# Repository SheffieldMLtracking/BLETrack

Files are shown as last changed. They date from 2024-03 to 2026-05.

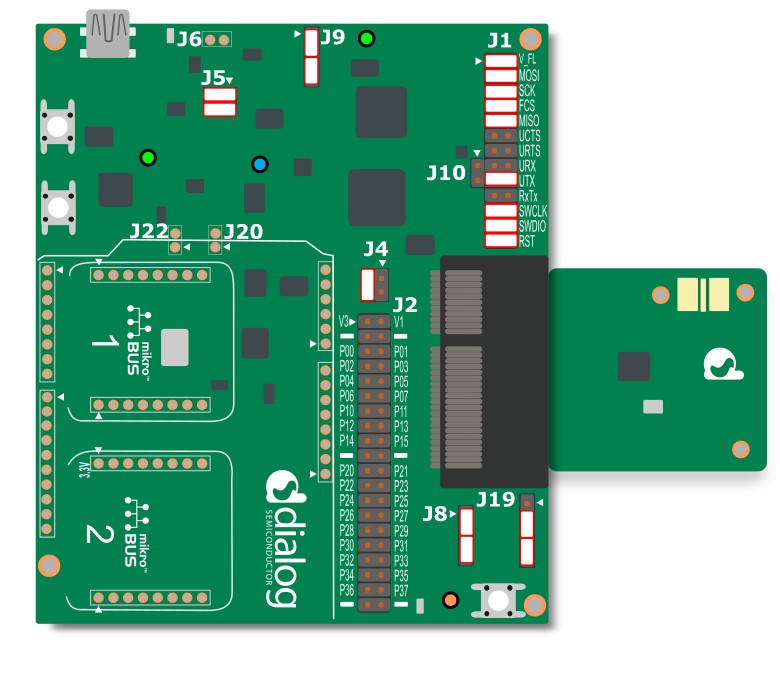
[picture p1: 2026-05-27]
Receiver/nestfinding adc recording/active_scanner/assets/da14585.jpg

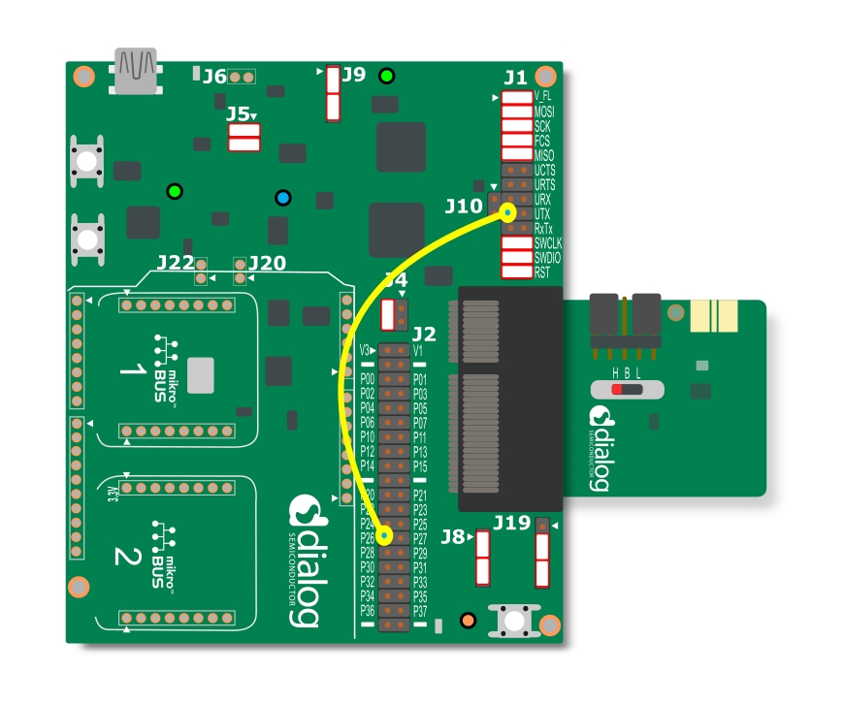
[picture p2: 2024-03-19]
Receiver/nestfinding adc recording/active_scanner/assets/da14531.jpg

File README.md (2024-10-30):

path

Code for Bluetooth Low Energy bee tracking system.

+ "Transmitter" folder contains the code to be flashed to the BT832X/BM832E transmitter board.
+ "Receiver" folder contains the code to be flashed to the DA14531 chip on-tag and the 'Active Scanner' code for testing & diagnostics.
+ "To Print" folder contains [FreeCAD](https://www.freecad.org/) files of the transmitter housing.
+ "Path Inference" folder contains code to process data from tag/dev board
+ Test data stored [here](https://github.com/SheffieldMLtracking/bluetooth_experiments)

## Notes on Programming Transmitter
### Transmitter programming:
+ Requires [nRF Connect SDK](https://www.nordicsemi.com/Products/Development-software/nRF-Connect-SDK).
+ Create a build for the nrf52dk_nrf52832 and add the included device tree overlay.
+ Connect nrf52dk and BT832X/BM832E to the computer via JLINK (done via micro USB cable). Connect DEBUG OUT on nrf52dk to DEBUG IN on BT832X/BM832E:nrf52dk_programming_example
+ flashthisfirst.c must be flashed to the BT832X/BM832E first - then main.c can be flashed.

NOTE: P0.31 is used for encoder output A, P0.30 for encoder output B and P0.11 for hall effect sensor input.

### Receiver programming:
+ Requires Keil uVision and configuration of environment as shown [here](https://lpccs-docs.renesas.com/UM-B-117-DA14531-Getting-Started-With-The-Pro-Development-Kit/01_abstract/abstract.html).
+ To program a receiver tag via flashing code to the OTP memory, follow [these](https://lpccs-docs.renesas.com/Tutorial_SDK6/otp_prog.html) instructions. **If you need to debug code on a tag, do not flash to the OTP.** DA14531 USB Development Kit can be used as a serial wire debug probe to debug code on an external DA14531 chip on the receiver tag using [this](https://lpccs-docs.renesas.com/Tutorial_SDK6/debug_probe.html) configuration of SWIO cables and DIP switches.
+ Note: binary for compiled DA14531 is found in Keil/DA14531_OUT/Objects.
+ Note: USB dev kit switches should be configured as shown: da14531_usb

## Usage of the System
### Setting Up Transmitters
+ Charge transmitters before field trial!
+ Each transmitter is placed onto a tripod across the landscape. The 0 degree point on the tripod (denoted by the small magnet on the base the transmitter sits in) should be pointed north using a compass before placing the transmitter itself upon the tripod. The transmitter should be level with the ground and mounted as high up as possible.
+ As each transmitter is turned on, the time between turning each on should be taken using a stop watch. This time is later used to zero the time readouts in the packets.
+ Using the "Active Scanner" code downloaded to the DA14531 USB Dev Kit, the serial output from the dev kit - which can be accessed using a serial terminal program such as Tera Term - should be used to verify the functionality of the tramsitters. The packets recieved by the active scanner are in the following form and should be assessed to ensure that the transmitter is in fact transmitting and that the motor is reading out ~360 degrees of rotation, resetting at the zero point. If there is an issue, the transmitter may need reprogramming, regarching or the motor encoder may have been knocked out of place.
Screenshot from 2024-10-29 13-43-06
+ Each transmitter currently has a range of approximately 100m (further at peak signal strength but not currently used in angle inference algorithm). The area tracked should be covered by at least 2, preferably 3 transmitters.

### Using a Receiever Tag
+ A programmed tag should be allowed to drain fully to hardware reset, then be charged and attatched to a bee.
+ Following retrieval, put the tag on charge and apply ground to the interrupt pin to switch the tag into transmit mode.
+ The data of each packet is encoded in the destination addr, in the same form as the transmitted packets except the RSSI of the packet is encoded in the leftmost byte. Using a bluetooth sniffer (reccomended [nrf52 BLE sniffer](https://www.nordicsemi.com/Products/Development-tools/nRF-Sniffer-for-Bluetooth-LE)) and Wireshark the transmitted packets can be read. The following filter shows only read packets:
<p align=center>btle.advertising_header.pdu_type == 0x01 && !_ws.expert && btle.advertising_address == 80:ea:ca:70:00:04</p>

### Performing Infernece
+ Instructions for performing path inference on data are located in PathInferenceFinalCut.inpyb

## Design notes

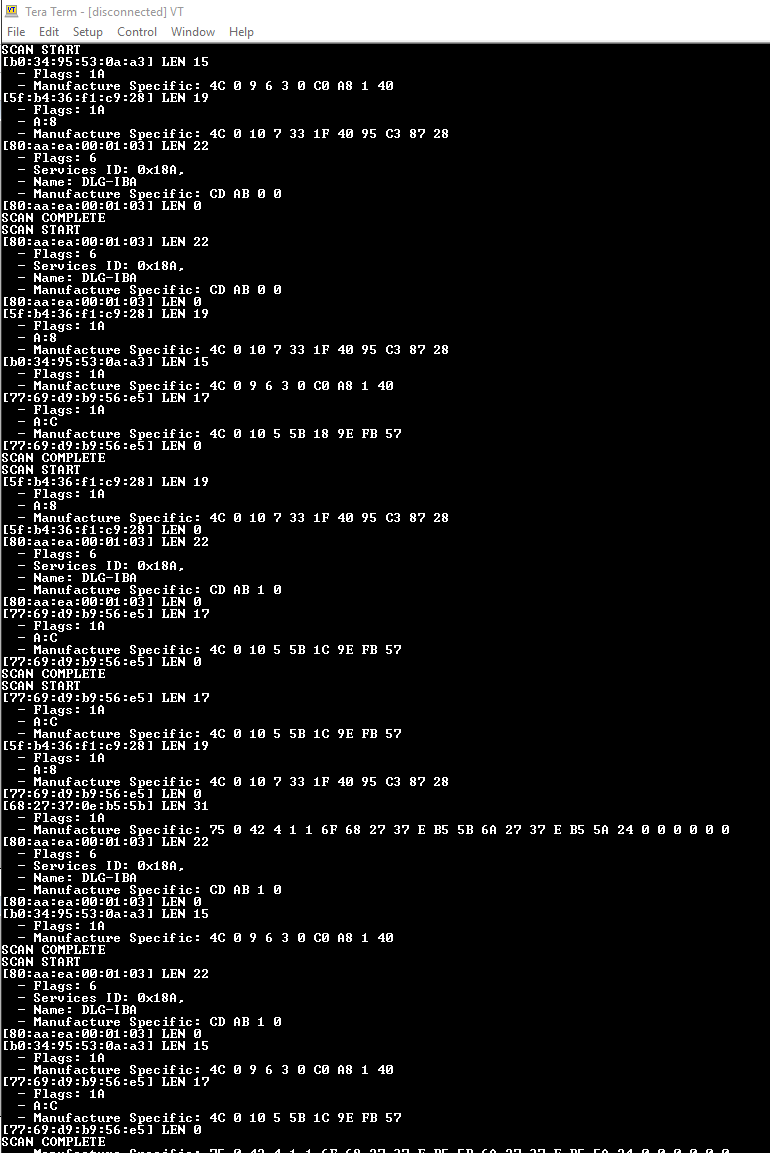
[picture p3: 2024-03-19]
Receiver/accel/active_scanner/assets/active_scanner.png

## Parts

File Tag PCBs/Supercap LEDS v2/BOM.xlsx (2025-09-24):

 |  |  | xxxx xxxx xxxxx xxPCS BOM (Sample Bill of Materials)
Item # | *Designator | *Qty | Manufacturer | *Mfg Part # | Description / Value | *Package/Footprint | Type | Your Instructions / Notes
1 | C1 | 2 | KYOCERA AVX | CM05X5R226M04AH | Multilayer Ceramic Capacitors SMD, 22 µF, 4V. [note if different cap is used: needs to be at least 3.6V, and as large as possible capacitance for the 0402 footprint]. | 0402 [1005 Metric] | SMD | Positive pin indicated with + (‘top’ end, nearest IC)
2 | U1 | 1 | Renesas / Dialog | DA14531-00000OG2 | Bluetooth Low Energy 5.1 SoC with integrated ARM Cortex M0+ | WLCSP-17 | SMD | Pin A1 indicated with dot (at top left, furthest from capacitor)
3 | Y1 | 1 | Seiko Semiconductors | ABM13W-32.0000MHZ-5-DH7G-T5 | 32.0000MHz Quartz Crystal. 5pF load cap. 7ppm freq tol. 15ppm freq stab. [requirements: Max drive power 100uW. Freq. Tol +/- 20ppm. Load cap 4-8pF. last time I used ABM13W-32.0000MHZ-5-D1G-T5 but this seems unavailable at the moment] | SMD (4 pins) | SMD | Pin 1 indicated by dot (nearest IC). Note that it is pin 2 that has notch in pad on crystal.
4 | C2 | 1 | Seiko Semiconductors | CPH3225A | Supercapacitor: electric double layer capacitor. 3.3V, 11mF, (internal impedance 160 Ohm). Size: 3.2 x 2.5 x 0.9. Weight: 24mg. | SMD (2 pins), 3.2mm x 2.5mm | SMD | Positive pin indicated with + and dot. Also shape of capacitor has notch on either side towards the negative end (indicated in silkscreen drawing). Negative terminal on capacitor has a diagonal notch (indicated by diagonal line on silkscreen by the pad).
5 | LED1 | 1 | Kingbright | KPG-0402SURKKC-TT | 0.45 mm x 0.25 mm SMD Hyper red LED, 0.2 mm thickness. AlGaInP on GaAs substrate Light Emitting Diode. Water clear lens. | 0402 [1005 Metric] | SMD | LED is placed in reverse bias, pin 1 goes to GND and pin 2 goes to a pin of part U1.
Need a quick and accurante quote? Need an efficient production? Please read SMT Ordering Necessary Files & Info in 1 minute. Thank you very much! (https://www.pcbway.com/smt_ordering_guide.html)
Click for Instructions on How to Create a BOM (https://www.pcbway.com/blog/PCB_Assembly/How_to_Build_a_BOM__Bill_Of_Materials_.html)

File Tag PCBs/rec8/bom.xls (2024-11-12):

PCBWay Bom Quotation, Product No.:T-2P6W461212A
Item # | *Designator | *Qty | Manufacturer | *Mfg Part # | Description / Value | *Package/Footprint | Mounting Type | Your Instructions / Notes | *Unit Price(3 sets) | *Total | *Delivery Time | *PCBWay Note | Customer Reply | PCBWay Update
1 | C1 | 8 | KYOCERA AVX | CM05X5R226M04AH | Multilayer Ceramic Capacitors SMD, 22 µF, 4V. [note if different cap is used: needs to be at least 3.6V, and as large as possible capacitance for the 0402 footprint]. | 0402 [1005 Metric] | SMD | Positive pin indicated with + (‘top’ end, nearest IC) | $1.146 | $27.504
2 | U1 | 8 | Renesas / Dialog | DA14531-00000OG2 | Bluetooth Low Energy 5.1 SoC with integrated ARM Cortex M0+ | WLCSP-17 | SMD | Pin A1 indicated with dot (at top left, furthest from capacitor) | $2.125 | $51.000 | 7-10 Workdays
3 | Y1 | 8 | ABRACON | ABM13W-32.0000MHZ-5-DH7G-T5 | 32.0000MHz Quartz Crystal. 5pF load cap. 7ppm freq tol. 15ppm freq stab. [requirements: Max drive power 100uW. Freq. Tol +/- 20ppm. Load cap 4-8pF. last time I used ABM13W-32.0000MHZ-5-D1G-T5 but this seems unavailable at the moment] | SMD (4 pins) | SMD | Pin 1 indicated by dot (nearest IC). Note that it is pin 2 that has notch in pad on crystal. | $3.457 | $82.968 | 7-10 Workdays
4 | C2 |  | Seiko Semiconductors | CPH3225A | Supercapacitor: electric double layer capacitor. 3.3V, 11mF, (internal impedance 160 Ohm). Size: 3.2 x 2.5 x 0.9. Weight: 24mg. | SMD (2 pins), 3.2mm x 2.5mm | SMD | Positive pin indicated with + and dot. Also shape of capacitor has notch on either side towards the negative end (indicated in silkscreen drawing). Negative terminal on capacitor has a diagonal notch (indicated by diagonal line on silkscreen by the pad).
 | A1 |  | Adafruit | 3522 | Hook-up Wire Enameled Copper Magnet Wire 0.1mm diameter. |  | Other | One end of a 70mm+/-10mm strand, soldered onto the 2mm x 1mm pad (indicated A1) on the front of the PCB (next to the IC and the crystal). The tip that is soldered might need the enamel removing before hand (e.g. heating). Let me know if this is a problem - or if you have a suggestion for non-enamelled wire we could use instead. (worst case we’ll attach the antenna ourselves). | (for 11m)
 |  |  |  |  |  |  |  |  | Component Cost | $161.47
 |  |  |  |  |  |  |  |  | Assembly Cost | $253.58
 |  |  |  |  |  |  |  | 6.728 | PCB Cost | $46.74
 |  |  |  |  |  |  |  |  | V1 Member 1% off | -$3.00
 |  |  |  |  |  |  |  |  | All Total 3 Sets | $458.79

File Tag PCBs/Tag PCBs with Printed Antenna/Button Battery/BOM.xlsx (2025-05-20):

 |  |  | xxxx xxxx xxxxx xxPCS BOM (Sample Bill of Materials)
Item # | *Designator | *Qty | Manufacturer | *Mfg Part # | Description / Value | *Package/Footprint | Type | Your Instructions / Notes
1 | C1 | 4 | KYOCERA AVX | CM05X5R226M04AH | Multilayer Ceramic Capacitors SMD, 22 µF, 4V. [note if different cap is used: needs to be at least 3.6V, and as large as possible capacitance for the 0402 footprint]. | 0402 [1005 Metric] | SMD | Positive pin indicated with + (‘top’ end, nearest IC)
2 | U1 | 40 | Renesas / Dialog | DA14531-00000OG2 | Bluetooth Low Energy 5.1 SoC with integrated ARM Cortex M0+ | WLCSP-17 | SMD | Pin A1 indicated with dot (at top left, furthest from capacitor)
3 | Y1 | 40 | ABRACON | ABM13W-32.0000MHZ-5-DH7G-T5 | 32.0000MHz Quartz Crystal. 5pF load cap. 7ppm freq tol. 15ppm freq stab. [requirements: Max drive power 100uW. Freq. Tol +/- 20ppm. Load cap 4-8pF. last time I used ABM13W-32.0000MHZ-5-D1G-T5 but this seems unavailable at the moment] | SMD (4 pins) | SMD | Pin 1 indicated by dot (nearest IC). Note that it is pin 2 that has notch in pad on crystal.
4 | A1 | 40 | Seiko Instruments | MS412FE FL26E | 3V 1mAh Rechargable Lithium Button Battery with PCB Pins | Other | Hand Soldered | Ground tab on battery is the left tab and should be hand soldered to the N1 pad on the PCB. +VE tab on battery is the right tab and should be hand soldered to the P1 pad on the PCB.
Need a quick and accurante quote? Need an efficient production? Please read SMT Ordering Necessary Files & Info in 1 minute. Thank you very much! (https://www.pcbway.com/smt_ordering_guide.html)
Click for Instructions on How to Create a BOM (https://www.pcbway.com/blog/PCB_Assembly/How_to_Build_a_BOM__Bill_Of_Materials_.html)

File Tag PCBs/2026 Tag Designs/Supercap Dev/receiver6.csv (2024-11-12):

Id | Designator | Footprint | Quantity | Designation | Supplier and ref
2 | Y1 | Crystal_SMD_Abracon_ABM13W-4Pin_1.2x1.0mm | 1 | Crystal_GND24
3 | U1 | DA14531_17-ball_WLCSP | 1 | DA14531_17-ball_WLCSP
4 | C1 | C_0402_1005Metric | 1 | C |  | ceramic Capacitor (22uF). e.g. GRM155R60J226ME11D
5 | REF** | CAPCP3225X100N_improved | 1 | CAPCP3225X100N_improved

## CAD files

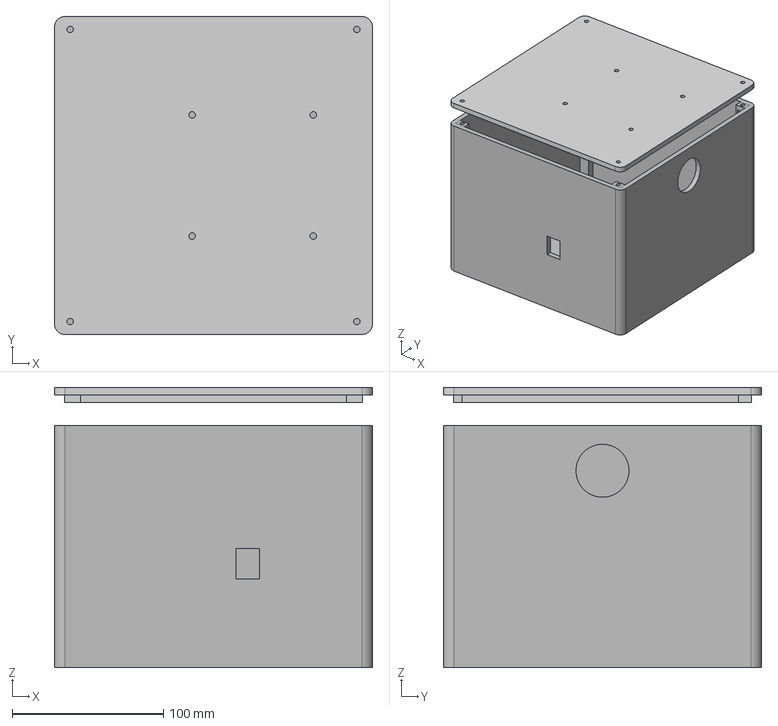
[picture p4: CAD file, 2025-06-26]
To Print/boxprototype.FCStd
210.0 x 210.0 x 185.0 mm
Lid

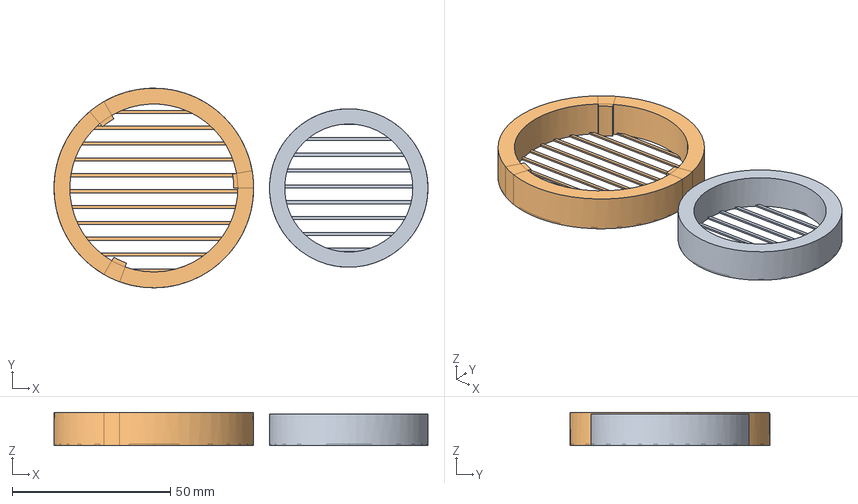
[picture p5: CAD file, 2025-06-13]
To Print/marking pot/doubletopmarkingpot.FCStd
118.0 x 63.0 x 10.5 mm
First Lid
Second Lid

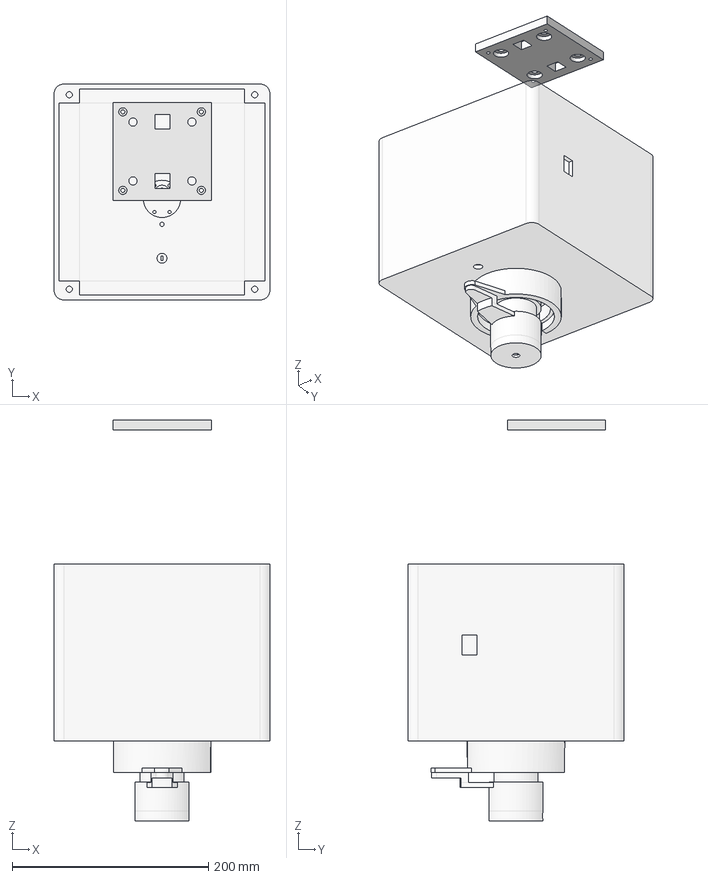
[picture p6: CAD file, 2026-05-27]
To Print/Transmitter 2026 Design/box2.FCStd
220.0 x 220.0 x 408.7 mm
MountToCase
MountToTripod

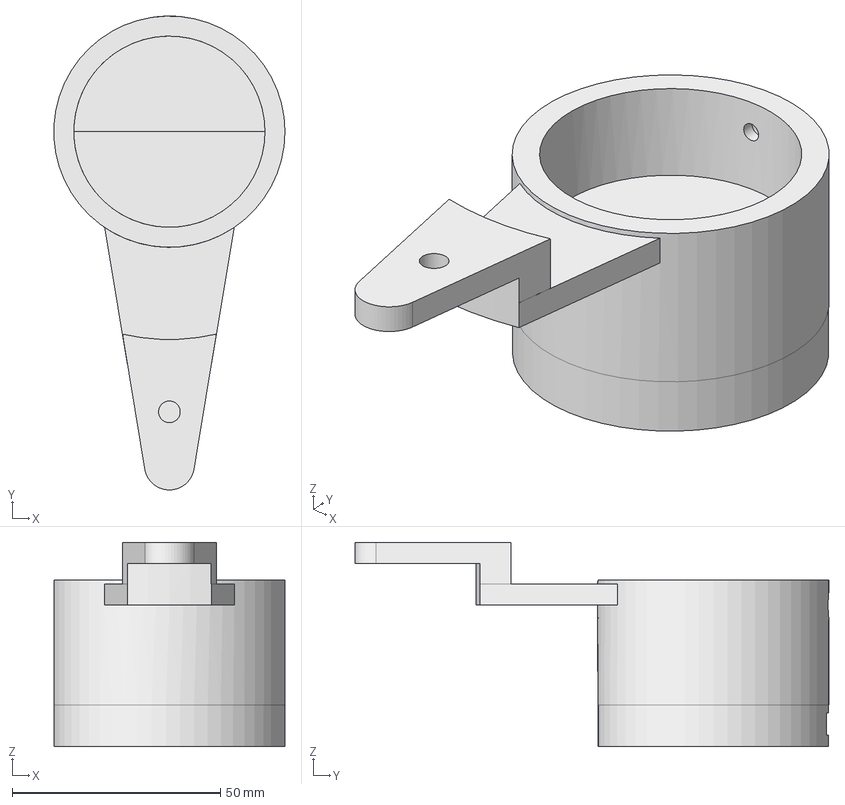
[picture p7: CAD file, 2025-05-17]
To Print/BoxMount.FCStd
55.4 x 113.7 x 49.0 mm

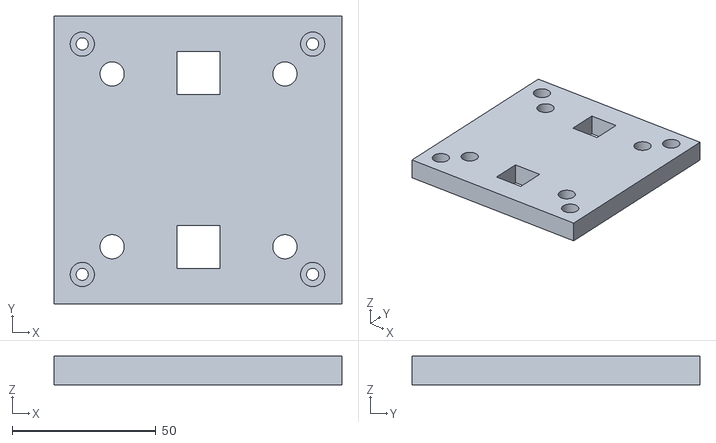
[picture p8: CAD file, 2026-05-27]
To Print/Transmitter 2026 Design/transmittermount.stl
100.0 x 100.0 x 10.0

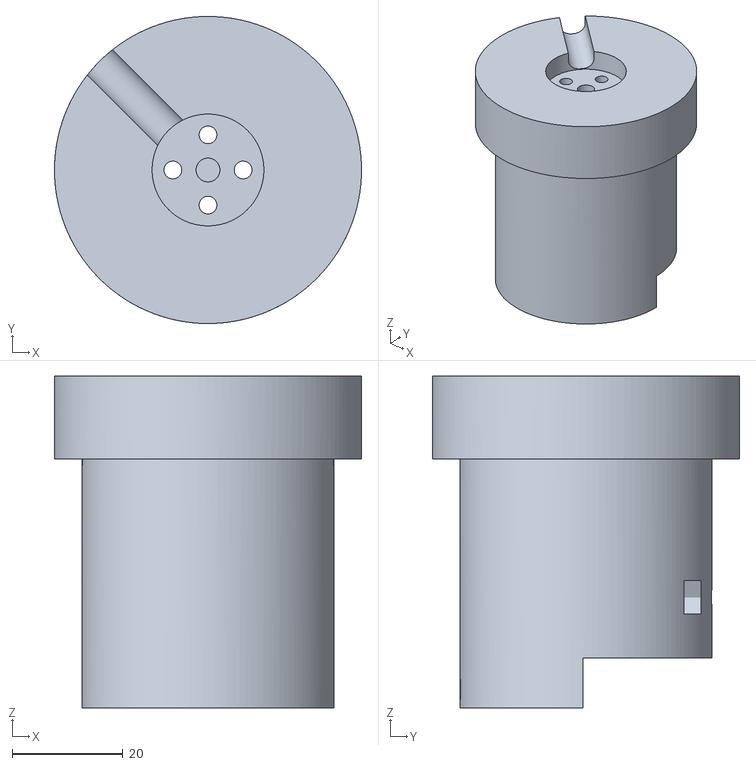
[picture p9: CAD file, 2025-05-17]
To Print/jun27stl.stl
55.5 x 55.5 x 60.0

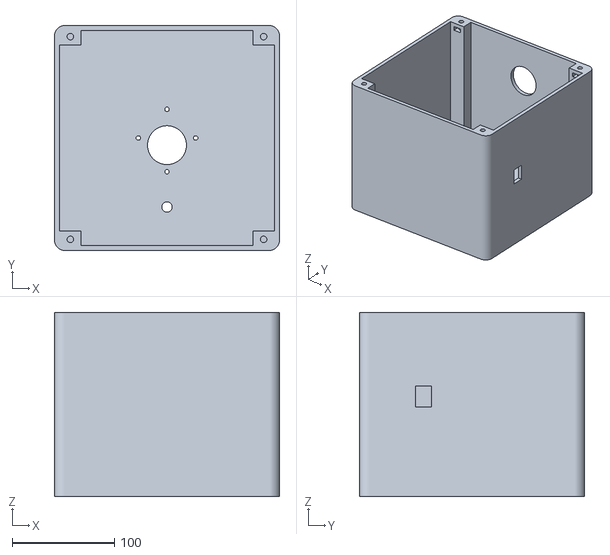
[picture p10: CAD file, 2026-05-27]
To Print/Transmitter 2026 Design/box2-Body.stl
220.0 x 220.0 x 180.0

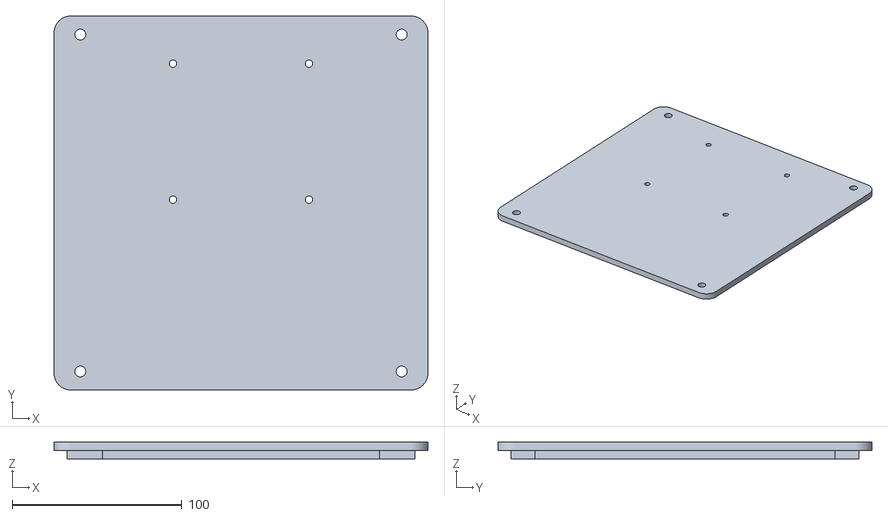
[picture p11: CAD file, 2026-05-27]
To Print/Transmitter 2026 Design/lid.stl
220.0 x 220.0 x 10.0

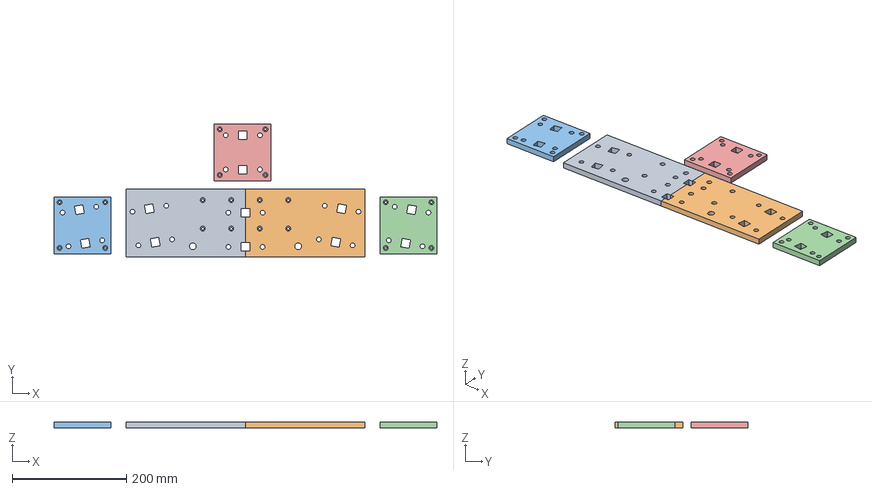
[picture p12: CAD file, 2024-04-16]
To Print/YagiMount.FCStd
671.7 x 233.9 x 10.0 mm
Body (Mirror #1)
Body001 (Mirror #2)

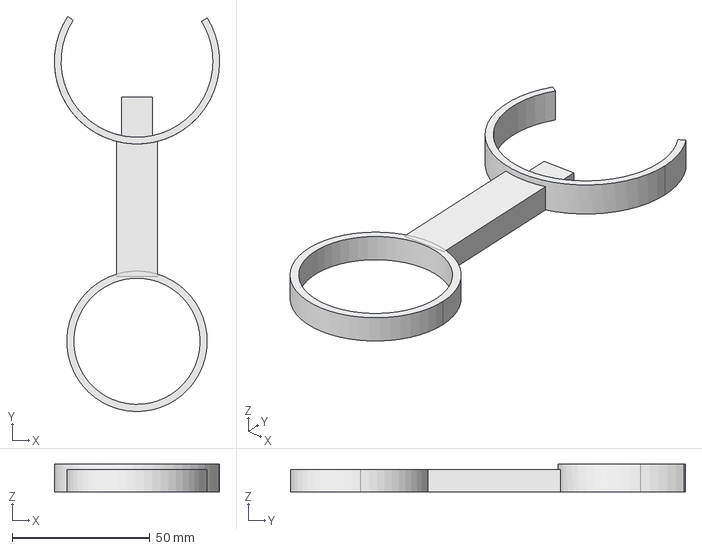
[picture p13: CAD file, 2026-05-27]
To Print/Transmitter 2026 Design/compas holder.FCStd
60.0 x 143.4 x 10.0 mm

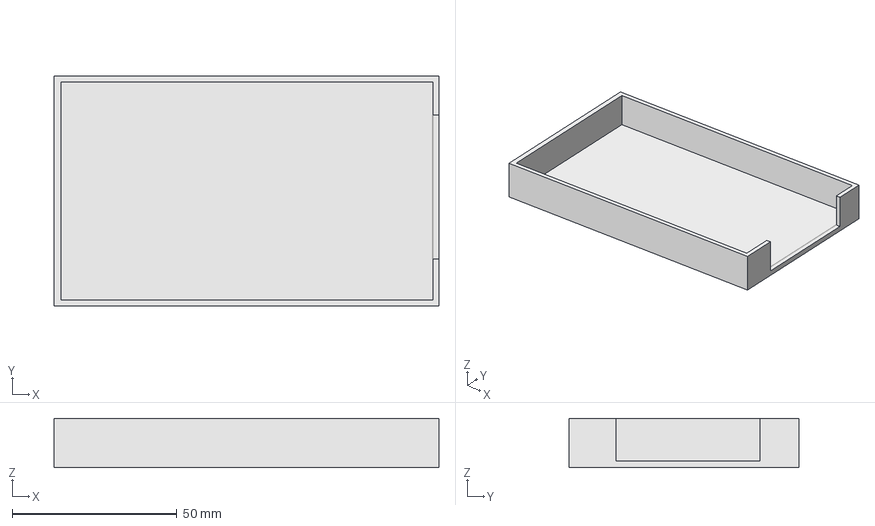
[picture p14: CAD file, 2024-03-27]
To Print/transmitterboardholder.FCStd
117.0 x 70.0 x 15.0 mm

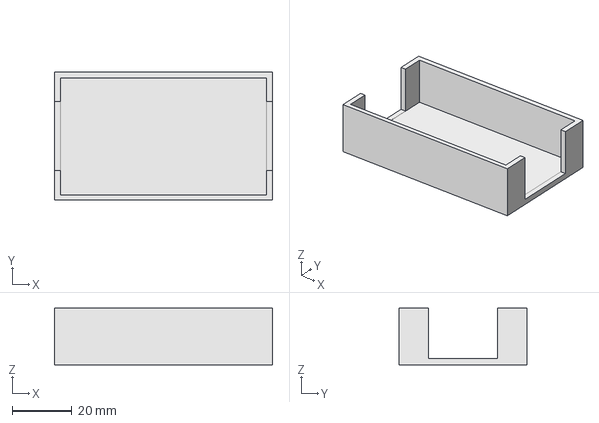
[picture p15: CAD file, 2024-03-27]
To Print/voltregholder.FCStd
73.0 x 43.0 x 19.0 mm

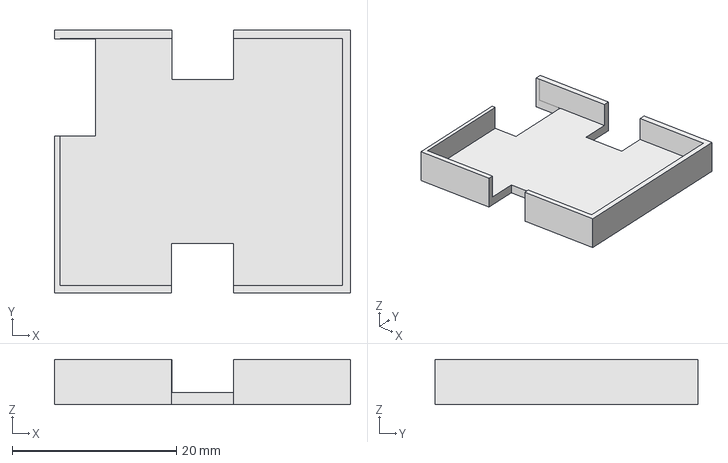
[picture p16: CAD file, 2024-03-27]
To Print/rfampcase.FCStd
36.0 x 32.0 x 5.50 mm

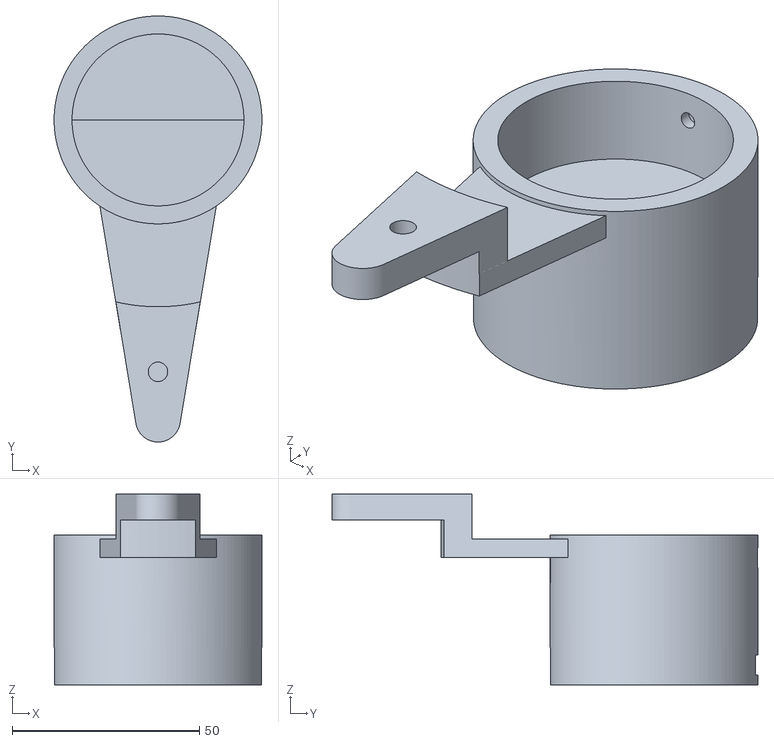
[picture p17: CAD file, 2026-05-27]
To Print/Transmitter 2026 Design/box2-MountToTripod.stl
55.5 x 113.7 x 51.0

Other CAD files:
To Print/Transmitter 2026 Design/compas holder-Fusion002.stl
To Print/Transmitter 2026 Design/voltregholder-Body.stl
To Print/Transmitter 2026 Design/doubletopmarkingpot-PartSecond Lid.stl
To Print/Transmitter 2026 Design/box2-MountToCase.stl
To Print/Transmitter 2026 Design/charging thing-Body.stl
To Print/Transmitter 2026 Design/charging thing-Body001.stl
To Print/Transmitter 2026 Design/doubletopmarkingpot-PartFirst Lid.stl
To Print/Transmitter 2026 Design/plug.stl
To Print/Transmitter 2026 Design/transmitterboardholder-Body.stl

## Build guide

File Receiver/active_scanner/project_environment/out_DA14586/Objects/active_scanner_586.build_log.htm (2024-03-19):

µVision Build Log

Tool Versions:

IDE-Version: µVision V5.38.0.0
Copyright (C) 2022 ARM Ltd and ARM Germany GmbH. All rights reserved.
License Information: Chris Noroozi, University of Sheffield, LIC=JGXHH-F3MSU-KGJ7N-B6QZF-X9RMT-7MG3X
 
Tool Versions:
Toolchain:       MDK-ARM Community  Version: 5.38.0.0
Toolchain Path:  C:\Keil_v5\ARM\ARM_Compiler_5.06u7\Bin
C Compiler:      Armcc.exe V5.06 update 7 (build 960)
Assembler:       Armasm.exe V5.06 update 7 (build 960)
Linker/Locator:  ArmLink.exe V5.06 update 7 (build 960)
Library Manager: ArmAr.exe V5.06 update 7 (build 960)
Hex Converter:   FromElf.exe V5.06 update 7 (build 960)
CPU DLL:         SARMCM3.DLL V5.38.0.0
Dialog DLL:      DARMCM1.DLL V1.19.6.0
Target DLL:      Segger\JL2CM3.dll V2.99.42.0
Dialog DLL:      TARMCM1.DLL V1.14.6.0

Project:

C:\Users\Chris\Desktop\active_scanner\project_environment\active_scanner.uvprojx
Project File Date:  10/24/2023

Output:

*** Using Compiler 'V5.06 update 7 (build 960)', folder: 'C:\Keil_v5\ARM\ARM_Compiler_5.06u7\Bin'
Build target 'DA14586'
assembling startup_DA14585_586.s...
compiling hardfault_handler.c...
compiling system_DA14585_586.c...
compiling nvds.c...
compiling nmi_handler.c...
compiling arch_console.c...
compiling hash.c...
compiling chacha20.c...
compiling arch_sleep.c...
compiling arch_main.c...
compiling jump_table.c...
compiling arch_rom.c...
compiling otp_hdr.c...
compiling syscntl.c...
compiling wkupct_quadec.c...
compiling adc_58x.c...
compiling arch_system.c...
compiling gpio.c...
compiling spi_58x.c...
compiling i2c.c...
compiling spi_flash.c...
compiling i2c_eeprom.c...
compiling dma.c...
compiling hw_otpc_58x.c...
compiling uart.c...
compiling trng.c...
compiling rf_531.c...
compiling ble_arp.c...
compiling attm_db_128.c...
compiling prf_utils.c...
compiling rwip.c...
compiling rf_585.c...
compiling diss.c...
compiling diss_task.c...
compiling custs1.c...
compiling custom_common.c...
compiling rwble.c...
compiling custs1_task.c...
compiling prf.c...
compiling app_security.c...
compiling app_task.c...
compiling app.c...
compiling app_default_handlers.c...
compiling app_security_task.c...
compiling app_bass.c...
compiling app_bass_task.c...
compiling app_findme.c...
compiling app_findme_task.c...
compiling app_proxr_task.c...
compiling app_proxr.c...
compiling app_diss.c...
compiling app_suotar.c...
compiling app_diss_task.c...
compiling app_suotar_task.c...
compiling app_msg_utils.c...
compiling app_easy_msg_utils.c...
compiling app_entry_point.c...
compiling app_easy_timer.c...
compiling app_easy_security.c...
compiling app_customs.c...
compiling app_customs_task.c...
compiling app_customs_common.c...
compiling app_utils.c...
compiling app_bond_db.c...
compiling user_custs1_def.c...
compiling user_custs_config.c...
compiling user_periph_setup.c...
compiling user_active_scanner.c...
.\..\..\..\..\..\sdk\platform\include\da14531.h(34): error:  #2571: invalid redefinition of enum "IRQn"  (declared at line 34 of ".\..\..\..\..\..\sdk\platform\include\da14585_586.h")
  typedef enum IRQn
.\..\..\..\..\..\sdk\platform\include\da14531.h(37): error:  #101: "NonMaskableInt_IRQn" has already been declared in the current scope
  NonMaskableInt_IRQn  = -14, /*  2 Non Maskable Interrupt Request.                              */
.\..\..\..\..\..\sdk\platform\include\da14531.h(38): error:  #101: "HardFault_IRQn" has already been declared in the current scope
  HardFault_IRQn       = -13, /*  3 Cortex-M0 Hard Fault Interrupt Request.                      */
.\..\..\..\..\..\sdk\platform\include\da14531.h(39): error:  #101: "SVCall_IRQn" has already been declared in the current scope
  SVCall_IRQn          = -5,  /* 11 Cortex-M0 SV Call Interrupt Request.                         */
.\..\..\..\..\..\sdk\platform\include\da14531.h(40): error:  #101: "PendSV_IRQn" has already been declared in the current scope
  PendSV_IRQn          = -2,  /* 14 Cortex-M0 Pend SV Interrupt Request.                         */
.\..\..\..\..\..\sdk\platform\include\da14531.h(41): error:  #101: "SysTick_IRQn" has already been declared in the current scope
  SysTick_IRQn         = -1,  /* 15 Cortex-M0 System Tick Interrupt Request.                     */
.\..\..\..\..\..\sdk\platform\include\da14531.h(44): error:  #101: "BLE_WAKEUP_LP_IRQn" has already been declared in the current scope
  BLE_WAKEUP_LP_IRQn   =  0,  /* Wakeup from Low Power Interrupt Request from BLE.               */
.\..\..\..\..\..\sdk\platform\include\da14531.h(45): error:  #101: "BLE_GEN_IRQn" has already been declared in the current scope
  BLE_GEN_IRQn         =  1,  /* BLE Interrupt Request. Sources:                                 */
.\..\..\..\..\..\sdk\platform\include\da14531.h(68): error:  #101: "UART_IRQn" has already been declared in the current scope
  UART_IRQn            =  2,  /* UART Interrupt Request.                                         */
.\..\..\..\..\..\sdk\platform\include\da14531.h(69): error:  #101: "UART2_IRQn" has already been declared in the current scope
  UART2_IRQn           =  3,  /* UART2 Interrupt Request.                                        */
.\..\..\..\..\..\sdk\platform\include\da14531.h(70): error:  #101: "I2C_IRQn" has already been declared in the current scope
  I2C_IRQn             =  4,  /* I2C Interrupt Request.                                          */
.\..\..\..\..\..\sdk\platform\include\da14531.h(71): error:  #101: "SPI_IRQn" has already been declared in the current scope
  SPI_IRQn             =  5,  /* SPI Interrupt Request.                                          */
.\..\..\..\..\..\sdk\platform\include\da14531.h(72): error:  #101: "ADC_IRQn" has already been declared in the current scope
  ADC_IRQn             =  6,  /* Analog-Digital Converter Interrupt Request.                     */
.\..\..\..\..\..\sdk\platform\include\da14531.h(73): error:  #101: "KEYBRD_IRQn" has already been declared in the current scope
  KEYBRD_IRQn          =  7,  /* Keyboard Interrupt Request.                                     */
.\..\..\..\..\..\sdk\platform\include\da14531.h(74): error:  #101: "BLE_RF_DIAG_IRQn" has already been declared in the current scope
  BLE_RF_DIAG_IRQn     =  8,  /* Baseband or Radio Diagnostics Interrupt Request. Required for   */
.\..\..\..\..\..\sdk\platform\include\da14531.h(78): error:  #101: "GPIO0_IRQn" has already been declared in the current scope
  GPIO0_IRQn           = 10,  /* GPIO Interrupt Request through debounce.                        */
.\..\..\..\..\..\sdk\platform\include\da14531.h(79): error:  #101: "GPIO1_IRQn" has already been declared in the current scope
  GPIO1_IRQn           = 11,  /* GPIO Interrupt Request through debounce.                        */
.\..\..\..\..\..\sdk\platform\include\da14531.h(80): error:  #101: "GPIO2_IRQn" has already been declared in the current scope
  GPIO2_IRQn           = 12,  /* GPIO Interrupt Request through debounce.                        */
.\..\..\..\..\..\sdk\platform\include\da14531.h(81): error:  #101: "GPIO3_IRQn" has already been declared in the current scope
  GPIO3_IRQn           = 13,  /* GPIO Interrupt Request through debounce.                        */
.\..\..\..\..\..\sdk\platform\include\da14531.h(82): error:  #101: "GPIO4_IRQn" has already been declared in the current scope
  GPIO4_IRQn           = 14,  /* GPIO Interrupt Request through debounce.                        */
.\..\..\..\..\..\sdk\platform\include\da14531.h(83): error:  #101: "SWTIM_IRQn" has already been declared in the current scope
  SWTIM_IRQn           = 15,  /* Software Timer (Timer0) Interrupt Request.                      */
.\..\..\..\..\..\sdk\platform\include\da14531.h(84): error:  #101: "WKUP_QUADEC_IRQn" has already been declared in the current scope
  WKUP_QUADEC_IRQn     = 16,  /* Combines the Wake up Capture Timer Interrupt Request,           */
.\..\..\..\..\..\sdk\platform\include\da14531.h(88): error:  #101: "DMA_IRQn" has already been declared in the current scope
  DMA_IRQn             = 19,  /* DMA Interrupt Request.                                          */
.\..\..\..\..\..\sdk\platform\include\da14531.h(90): error:  #101: "RESERVED21_IRQn" has already been declared in the current scope
  RESERVED21_IRQn      = 21,  /* SoftWare Interrupt Request.                                     */
.\..\..\..\..\..\sdk\platform\include\da14531.h(91): error:  #101: "RESERVED22_IRQn" has already been declared in the current scope
  RESERVED22_IRQn      = 22,  /* SoftWare Interrupt Request.                                     */
.\..\..\..\..\..\sdk\platform\include\da14531.h(92): error:  #101: "RESERVED23_IRQn" has already been declared in the current scope
  RESERVED23_IRQn      = 23,  /* SoftWare Interrupt Request.                                     */
.\..\..\..\..\..\sdk\platform\include\da14531.h(93): error:  #256: invalid redeclaration of type name "IRQn_Type"  (declared at line 93 of ".\..\..\..\..\..\sdk\platform\include\da14585_586.h")
  } IRQn_Type;
.\..\..\..\..\..\sdk\platform\include\da14531.h(130): warning:  #47-D: incompatible redefinition of macro "FUNC_SPI_DI"  (declared at line 109 of ".\..\..\..\..\..\sdk\platform\include\da14585_586.h")
  #define FUNC_SPI_DI        (26)
.\..\..\..\..\..\sdk\platform\include\da14531.h(131): warning:  #47-D: incompatible redefinition of macro "FUNC_SPI_DO"  (declared at line 110 of ".\..\..\..\..\..\sdk\platform\include\da14585_586.h")
  #define FUNC_SPI_DO        (27)
.\..\..\..\..\..\sdk\platform\include\da14531.h(132): warning:  #47-D: incompatible redefinition of macro "FUNC_SPI_CLK"  (declared at line 111 of ".\..\..\..\..\..\sdk\platform\include\da14585_586.h")
  #define FUNC_SPI_CLK       (28)
.\..\..\..\..\..\sdk\platform\include\da14531.h(171): error:  #101: "__CLK_REF_SEL_REG" has already been declared in the current scope
  struct __CLK_REF_SEL_REG
.\..\..\..\..\..\sdk\platform\include\da14531.h(188): error:  #101: "__CLK_REF_CNT_REG" has already been declared in the current scope
  struct __CLK_REF_CNT_REG
.\..\..\..\..\..\sdk\platform\include\da14531.h(201): error:  #101: "__CLK_REF_VAL_L_REG" has already been declared in the current scope
  struct __CLK_REF_VAL_L_REG
..\src\user_active_scanner.c: 3 warnings, 30 errors
".\out_DA14586\Objects\active_scanner_586.axf" - 30 Error(s), 3 Warning(s).

Software Packages used:

Package Vendor: ARM
                http://www.keil.com/pack/ARM.CMSIS.5.9.0.pack
                ARM.CMSIS.5.9.0
                CMSIS (Common Microcontroller Software Interface Standard)

Collection of Component include folders:

  C:/Users/Chris/AppData/Local/Arm/Packs/ARM/CMSIS/5.9.0/Device/ARM/ARMCM0/Include

Collection of Component Files used:

Target not created.
Build Time Elapsed:  00:00:16

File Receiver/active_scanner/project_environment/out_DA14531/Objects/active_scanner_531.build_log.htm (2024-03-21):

µVision Build Log

Tool Versions:

IDE-Version: µVision V5.38.0.0
Copyright (C) 2022 ARM Ltd and ARM Germany GmbH. All rights reserved.
License Information: Chris Noroozi, University of Sheffield, LIC=JGXHH-F3MSU-KGJ7N-B6QZF-X9RMT-7MG3X
 
Tool Versions:
Toolchain:       MDK-ARM Community  Version: 5.38.0.0
Toolchain Path:  C:\Keil_v5\ARM\ARM_Compiler_5.06u7\Bin
C Compiler:      Armcc.exe V5.06 update 7 (build 960)
Assembler:       Armasm.exe V5.06 update 7 (build 960)
Linker/Locator:  ArmLink.exe V5.06 update 7 (build 960)
Library Manager: ArmAr.exe V5.06 update 7 (build 960)
Hex Converter:   FromElf.exe V5.06 update 7 (build 960)
CPU DLL:         SARMCM3.DLL V5.38.0.0
Dialog DLL:      DARMCM1.DLL V1.19.6.0
Target DLL:      Segger\JL2CM3.dll V2.99.42.0
Dialog DLL:      TARMCM1.DLL V1.14.6.0

Project:

C:\Users\Chris\Desktop\active_scanner\project_environment\active_scanner.uvprojx
Project File Date:  03/20/2024

Output:

*** Using Compiler 'V5.06 update 7 (build 960)', folder: 'C:\Keil_v5\ARM\ARM_Compiler_5.06u7\Bin'
Build target 'DA14531'
compiling user_active_scanner.c...
..\src\user_active_scanner.c(310): warning:  #128-D: loop is not reachable
  	while( index < param->report.data_len) {
..\src\user_active_scanner.c(344): warning:  #128-D: loop is not reachable
  	while( index < param->report.data_len) {
..\src\user_active_scanner.c: 2 warnings, 0 errors
linking...
Program Size: Code=18568 RO-data=3176 RW-data=12 ZI-data=13892  
FromELF: creating hex file...
After Build - User command #1: fromelf --bincombined --output=".\out_DA14531\Objects\active_scanner_531.bin"  ".\out_DA14531\Objects\active_scanner_531.axf"
".\out_DA14531\Objects\active_scanner_531.axf" - 0 Error(s), 2 Warning(s).

Software Packages used:

Package Vendor: ARM
                http://www.keil.com/pack/ARM.CMSIS.5.9.0.pack
                ARM.CMSIS.5.9.0
                CMSIS (Common Microcontroller Software Interface Standard)

Collection of Component include folders:

  C:/Users/Chris/AppData/Local/Arm/Packs/ARM/CMSIS/5.9.0/Device/ARM/ARMCM0plus/Include

Collection of Component Files used:

Build Time Elapsed:  00:00:03

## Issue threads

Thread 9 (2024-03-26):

### ISSUE TITLE
Flashing to DA14531

### ISSUE THREAD

**Issue by ChrisYeen** [SheffieldMLtracking/BLETrack#9]
How to do this?

**Comment by FloofyDwagon** [comment]
DA14531 doesn't have flash memory - have to program to OTP memory as shown here: https://lpccs-docs.renesas.com/Tutorial_SDK6/otp_prog.html

Worth noting the following:

> The ROM-based bootloader on the DA1453x does not activate the SWD ( [Serial Wire Debug Probe](https://lpccs-docs.renesas.com/Tutorial_SDK6/debug_probe.html#serial-wire-debug)) interface during the OTP-to-RAM loading process. Consequently, once you program your application into OTP on the DA14531, SWD interface access to the device is no longer possible. Additionally, it’s crucial to exercise caution when programming OTP on the DA14585/86, as incorrect programming can render the device unusable. Follow these instructions meticulously to ensure proper execution.

**Comment by ChrisYeen** [comment]
DA14531 doesn't have flash memory - have to program to OTP memory as shown here: https://lpccs-docs.renesas.com/Tutorial_SDK6/otp_prog.html

Worth noting the following:

> The ROM-based bootloader on the DA1453x does not activate the SWD ( [Serial Wire Debug Probe](https://lpccs-docs.renesas.com/Tutorial_SDK6/debug_probe.html#serial-wire-debug)) interface during the OTP-to-RAM loading process. Consequently, once you program your application into OTP on the DA14531, SWD interface access to the device is no longer possible. Additionally, it’s crucial to exercise caution when programming OTP on the DA14585/86, as incorrect programming can render the device unusable. Follow these instructions meticulously to ensure proper execution.

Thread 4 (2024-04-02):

### ISSUE TITLE
Transmission power?

### ISSUE THREAD

**Issue by ChrisYeen** [SheffieldMLtracking/BLETrack#4]
Can the power of transmission be configured via the CONFIG_BT_CTLR_TX_PWR_ANTENNA attribute in Transmitter/prj.conf to be higher than the default but within the viable range for the [RF amp](https://www.ebay.co.uk/itm/394782255776?mkevt=1&mkpid=0&emsid=e11050.m43.l1123&mkcid=7&ch=osgood&euid=d541b1dd0cbc4e4bbd2ea76060c029a0&bu=44741448833&osub=-1~1&crd=20231218030503&segname=11050) (and will not cause saturation?).

**Comment by ChrisYeen** [comment]
BT840 transmission power information: https://www.fanstel.com/bt840

8dBm max? Probably too high for the RF amp.

**Comment by lionfish0** [comment]
Aren't we using the [BT832XE](https://www.fanstel.com/s/BT832X-p-Product-Specifications.pdf)? which has a 20dBm power output:

![image](https://github.com/SheffieldMLtracking/BLETrack/assets/7914304/d6c4c2da-fe94-400a-8c43-9e0173caad2a)

as you say, this will be too high, as the RF amplifier doesn't want more that, I think, 3dBm as input (to avoid saturation). This also means we should look again at which bluetooth module we should use (I think I chose the BT832XE because of its high power output, that we don't need any more, as we have the 30dB RF amplifier).

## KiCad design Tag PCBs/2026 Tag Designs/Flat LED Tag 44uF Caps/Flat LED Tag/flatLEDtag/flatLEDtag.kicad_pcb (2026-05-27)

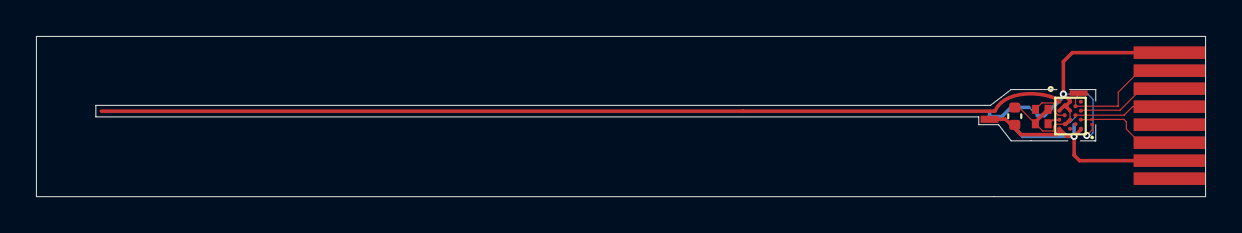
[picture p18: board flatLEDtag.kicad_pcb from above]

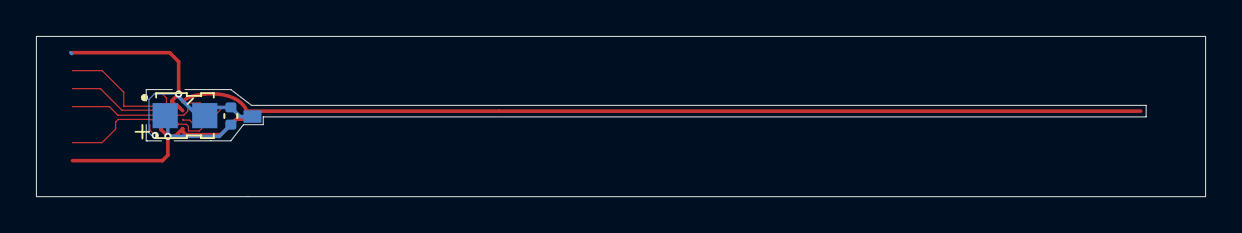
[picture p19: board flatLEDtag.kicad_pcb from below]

Board: 2 copper layers, 64.9 x 8.9 mm, 8 parts (2 on the bottom side), 9 nets.

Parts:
AE1: Antenna
C1, C3: C; C_0402_1005Metric
C2: CPH3225A; CAPCP3225X100N_improved
D1: LED; KPG-0402SURKKC-TT
J1: Conn_01x08; FPC_1x08_P1.00mm_plug_3mm
U1: DA14531_17-ball_WLCSP
Y1: Crystal_GND24; Crystal_SMD_Abracon_ABM13W-4Pin_1.2x1.0mm

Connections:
/+VE: C1.1, C2.1, C3.1, J1.7, U1.G1 (VBAT_LOW), U1.G5 (VBAT_HIGH)
/GND: C1.2, C2.2, C3.2, D1.1 (K), J1.1, U1.A3 (RFIOm), U1.C1 (GND_RF2), U1.C3 (GND_RF1), U1.E3 (VSS), U1.F2 (GND_DCDC), Y1.2, Y1.4
/IR: J1.2, U1.B4 (P0_3/XTAL32kp)
/LED +VE: D1.2 (A), J1.6, U1.E5 (P0_1/ADC0/SWDIO)
unnamed: J1.3, U1.C5 (P0_2/ADC1/SWCLK)
unnamed: J1.4, U1.D4 (P0_5/SWDIO)
unnamed: J1.5, U1.F4 (P0_0/RST)
unnamed: U1.E1 (XTAL32Mm), Y1.3
unnamed: U1.D2 (XTAL32Mp), Y1.1

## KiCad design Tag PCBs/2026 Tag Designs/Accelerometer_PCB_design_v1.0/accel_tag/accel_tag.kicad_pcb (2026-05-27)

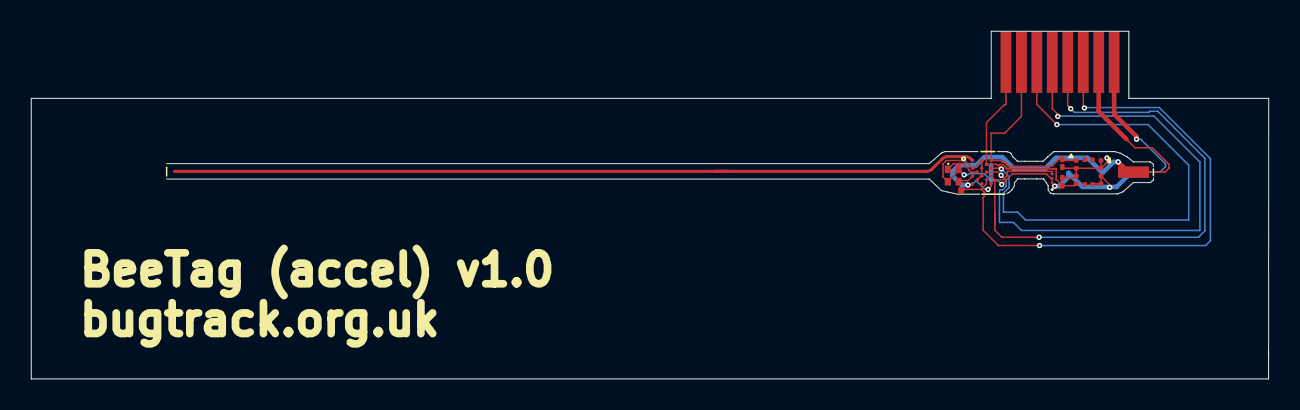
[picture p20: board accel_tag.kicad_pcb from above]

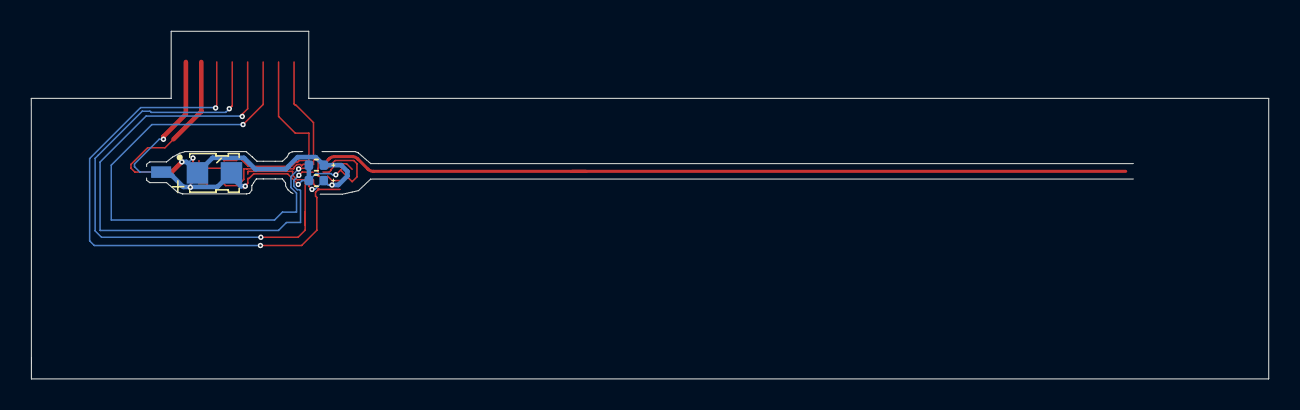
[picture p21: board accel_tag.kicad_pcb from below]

Board: 2 copper layers, 80.1 x 22.5 mm, 14 parts (4 on the bottom side), 10 nets.

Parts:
AE1: Antenna
C1: CPH3225A; CAPCP3225X100N_improved
C2, C3: C_Polarized; C_0402_1005Metric
CHARGING_GND1: Charging ground pin; Charging_pad_0.75x2mm
CHARGING_POSITIVE1: Charging positive pin; Charging_pad_0.75x2mm
D1: LED; KPG-0402SURKKC-TT
J1: Conn_01x08; FPC_1x08_P1.00mm_plug_3mm
R1, R2: 10K; R_01005_0402Metric
TP1: TestPoint; TestPoint_Pad_1.0x1.0mm
U1: LIS2DU12TR; LGA-12L_LIS2DU12_STM
U2: DA14531-00000OG2; DA14531_17-ball_WLCSP
Y1: ABM13W-32MHz; Crystal_SMD_Abracon_ABM13W-4Pin_1.2x1.0mm

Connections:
GNDREF: C1.2, C2.2, C3.2, CHARGING_GND1.1, D1.1 (K), J1.8, U1.6 (GND), U1.7 (RES), U1.8 (GND), U2.A3 (RFIOM), U2.C1 (GND_RF2), U2.C3 (GND_RF1), U2.E3 (VSS), U2.F2 (GND_DCDC), Y1.2 (GND), Y1.4 (NC)
unnamed: D1.2 (A), J1.5, U2.E5 (P0_1/ADC0/SWDIO)
unnamed: J1.1, R2.2, U1.4 (SDA/SDI/SDO), U2.B4 (P0_3/XTAL32KP)
unnamed: J1.2, R1.2, U1.1 (SCL/SPC), U2.A5 (P0_4/XTAL32KM)
unnamed: J1.3, U2.C5 (P0_2/ADC1/SWCLK)
unnamed: J1.4, U2.D4 (P0_5/SWDIO)
unnamed: J1.6, TP1.1, U2.F4 (RST/P0_0)
unnamed: C1.1, C2.1, C3.1, CHARGING_POSITIVE1.1, J1.7, R1.1, R2.1, U1.2 (CS), U1.3 (SDO/SA0), U1.9 (VDD), U1.10 (VDD_IO), U2.G1 (VBAT_LOW), U2.G5 (VBAT_HIGH)
unnamed: U2.E1 (XTAL32MM), Y1.3
unnamed: U2.D2 (XTAL32MP), Y1.1

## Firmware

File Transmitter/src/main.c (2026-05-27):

//prj.conf settings are required for this to function

#include <zephyr/types.h>
#include <stddef.h>
#include <string.h>
#include <errno.h>
#include <zephyr/sys/printk.h>
#include <zephyr/sys/byteorder.h>
#include <zephyr/sys/reboot.h>
#include <zephyr/settings/settings.h>
#include <zephyr/bluetooth/bluetooth.h>
#include <zephyr/bluetooth/hci.h>
#include <zephyr/bluetooth/conn.h>
#include <zephyr/bluetooth/uuid.h>
#include <zephyr/bluetooth/gatt.h>
#include <zephyr/device.h>
#include <zephyr/drivers/sensor.h>
#include <zephyr/drivers/gpio.h>

static struct bt_le_adv_param adv_param; // Holds params for advertising
static bt_addr_le_t bond_addr; // Address to advertise to (reciever address)
static bt_addr_le_t identity_zero_addr; // Adress to initialize default ID 
static bt_addr_le_t transmit_addr; // Address to transmit from (transmitter address)

// For the qdec to work with the motor, navigate to where your nrf connect toolchain is located, go to the nrfx_qdec folder...
// and in the .c file set the following under .config{}:
//	.reportper = NRF_QDEC_REPORTPER_10,
//	.sampleper = NRF_QDEC_SAMPLEPER_128US,
struct sensor_value val;
const struct device *const dev = DEVICE_DT_GET(DT_ALIAS(qdec0));

#define HE0_NODE DT_ALIAS(sw0)
static const struct gpio_dt_spec HESensor = GPIO_DT_SPEC_GET(HE0_NODE, gpios);
static struct gpio_callback halleffect_cb_data;

int currentAngle = 0; // Stores angle of rotation
int actualDegrees = 0;
bool hallEffectTriggerFlag = false;

// ---------------------------- HALL EFFECT INTERRUPT -------------------------

void halleffect_cb(const struct device *dev, struct gpio_callback *cb,
                    uint32_t pins)
{
	if (!hallEffectTriggerFlag)
	{
		//printk("HE triggered");
		currentAngle = 0;
		actualDegrees = 0;
		hallEffectTriggerFlag = true;
	}
}

// ---------------------------- DIRECT ADVERTISING ----------------------------

// Ensures settings are loaded
static void bt_ready(void)
{
	printk("Bluetooth initialized\n");
	if (IS_ENABLED(CONFIG_SETTINGS)) {
		settings_load();
	}
}

int main(void)
{
	gpio_pin_configure_dt(&HESensor, GPIO_INPUT);
	gpio_pin_interrupt_configure_dt(&HESensor, GPIO_INT_EDGE_BOTH);
	gpio_init_callback(&halleffect_cb_data, halleffect_cb, BIT(HESensor.pin));
	gpio_add_callback(HESensor.port, &halleffect_cb_data);

	int err;
	// NOTE: ID creation should be before bt_enable to get around IRK (I think) and privacy must be turned off in the config
	// Create ID 0, this is needed (I think?) but the identity does not get used
	bt_addr_le_from_str("DA:EE:AA:FF:FF:41", "random", &identity_zero_addr); // Has to be different to ID 1 upon initialization
 	err = bt_id_create(&identity_zero_addr, NULL);
	// Debug output
 	if (err < 0) {
 		printk("Creating new ID 0 failed (err %d)\n", err);
 	}

	// Create ID 1, this is the identity we will use for transmission
	bt_addr_le_from_str("DA:EE:AA:FF:FF:00", "random", &transmit_addr);
	err = bt_id_create(&transmit_addr, NULL); 
	// Debug output
 	if (err < 0) {
 		printk("Creating new ID 1 failed (err %d)\n", err);
 	}

	// Enable bluetooth connectivity
	err = bt_enable(NULL);
	// Debug output
	if (err) {
		printk("Bluetooth init failed (err %d)\n", err);
		return 0;
	}

	// Begin advertisement
	bt_ready();

	while (1) {
		char toAddrOutput[BT_ADDR_LE_STR_LEN];
		char fromAddrOutput[BT_ADDR_LE_STR_LEN];

		// Copy reciever address to a variable
		bt_addr_le_copy(&bond_addr, BT_ADDR_LE_NONE); 
		bt_addr_le_from_str("80:EA:CA:70:00:04", "public", &bond_addr);

		bt_le_adv_stop(); // Stop advertising here to change value of transmitter address before transmission
		
		sensor_sample_fetch(dev);
		sensor_channel_get(dev, SENSOR_CHAN_ROTATION, &val);

		actualDegrees += val.val1;
		currentAngle = actualDegrees/(150);
		if (currentAngle > 100)
		{
			hallEffectTriggerFlag = false;
		}
		
		
		if (currentAngle >= 360)
		{
			actualDegrees = actualDegrees - (360 * 150);
			currentAngle = 0;
		}
		
		//printk("Position = %d degrees\n", currentAngle);

		
		
		//transmit_addr.a.val[0]=transmit_addr.a.val[0]+1; // Alter transmitter address
		int uniqueID = 8;
		int angleHex = (currentAngle - (currentAngle % 16)) / 16;
		int angleRemainder = currentAngle % 16;

		// Get current clock cycle (clsock runs at 32768 Hz on nrf52dk_nrf52832 & (presumably) on the EV-BT832X)
		int systemClockSpeed = 32768;
		uint32_t systemClock = k_cycle_get_32() / (systemClockSpeed / 100); // Divide to give 10ms accuracy.

		// Transmitted Packets are in the format:
			// 00 : First Two Hex Digits of Time : Next Two Hex Digits of Time : Last Two Hex Digits of Time : First Two Hex Digits of Angle : Last Hex Digit of Angle & ID
		transmit_addr.a.val[4] = systemClock / 65536;
		transmit_addr.a.val[3] = (systemClock % 65536) / 256;
		transmit_addr.a.val[2] = systemClock % 256;
		transmit_addr.a.val[1] = angleHex;
		transmit_addr.a.val[0] = uniqueID + (angleRemainder * 16);

		//transmit_addr.a.val[0] = uniqueID;
		//transmit_addr.a.val[1] = transmit_addr.a.val[1] + 1;
		bt_id_reset(1,&transmit_addr, NULL); // Update ID with new transmitter address

		// Debug output addresses
		//bt_addr_le_to_str(&bond_addr, toAddrOutput, sizeof(toAddrOutput));
		//bt_addr_le_to_str(&transmit_addr, fromAddrOutput, sizeof(fromAddrOutput));
		//printk("Direct advertising to %s from %s\n", toAddrOutput, fromAddrOutput);

		// Send direct advertisment
		adv_param = *BT_LE_ADV_CONN_DIR(&bond_addr); // Advertise to reciever address
		adv_param.id=1; // Set to ID 1 - this is the ID we are using to set our transmitter address
		err = bt_le_adv_start(&adv_param, NULL, 0, NULL, 0);

		// Output debug error
		//if (err) {
			//printk("Advertising failed to start (err %d)\n", err);
		//} else {
			//printk("Advertising successfully started\n");
		//}	
		k_msleep(10);
	}
	return 0;
}

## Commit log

2024-03-26 Added Hall Effect IR
    Resets angle of encoder readout when HE is triggered, uses pin 11 and SW0 gpio-ir
2024-03-27 Yagi Mount File
    [YagiMount.FCStd]
2024-03-27 Alleviated Motor Drift
    Angle readout stored and processed as float - rounding was a source of drift. Also updated angle conversion to use 488.3:1 ratio as reported by the 488:1 Metal Gearmotor 20Dx46L mm 12V CB with Extend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
2024-03-27 Set Transmission Power to 3dBm
    CONFIG_BT_CTLR_TX_PWR_ANTENNA added and set
2024-03-27 Added rest of FCStd files
    [BoxMount.FCStd, boxprototype.FCStd, rfampcase.FCStd, transmitterboardholder.FCStd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]
2024-04-02 Motor Drift Fix w/o Floating Points
2024-04-03 size adjustments
    [BoxMount.FCStd, boxprototype.FCStd]
2024-04-16 Added support for longer mount
    [YagiMount.FCStd]
2024-05-22 Fixed HE pin
2024-05-22 Improved HE sensor through hole
    [boxprototype.FCStd]
2024-06-26 Fixed HE and tripod mount issues
    [BoxMount.FCStd]
2024-11-12 PCB old version
    [BOM.xlsx, bom.xls, receiver6.csv, receiver6.kicad_pcb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]
2025-06-13 Initial (untested) version of the marking pot
    [doubletopmarkingpot.FCStd]
2025-09-24 Upload LED tags
    [BOM.xlsx, receiver6.csv, receiver6.kicad_pcb]
2026-03-19 fix path that doesn't work in windows
    [BOM.xlsx, receiver6-B_Cu.gbr, receiver6-B_Mask.gbr, receiver6-B_Paste.gbr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]
2026-03-19 remove broken path name
    [BOM.xlsx, receiver6-B_Cu.gbr, receiver6-B_Mask.gbr, receiver6-B_Paste.gbr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]
2026-05-27 new tag designs
    [BOM-2.xlsx, flatLEDtag-B_Cu.gbr, flatLEDtag-B_Mask.gbr, flatLEDtag-B_Paste.gbr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]
